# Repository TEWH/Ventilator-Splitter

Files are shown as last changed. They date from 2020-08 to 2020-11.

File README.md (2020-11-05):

Last updated: 9/7/20

NOTE: This is an independent project that is not affiliated with any commercial institution.

# **Table of Contents**
- [Disclaimers](#disclaimers)
- [Background + Why it’s needed](#background-+-why-it’s-needed)
- [Government Policies for Ventilators during COVID-19](#government-policies-for-ventilators-during-covid-19)
- [Materials](#materials)
- [Bill of Materials](#bill-of-materials)
- [Overall Design](#overall-design)
	- [Circuit Design](#circuit-design)
	- [Sensors](#sensors)
- [Electronically-Regulated Valves](#electronically-regulated-valves)
- [Software Design (Valve Control)](#software-design-(valve-control))
- [App Design](#app-design)
- [Low-cost Spirometer](#low-cost-spirometer)
	- [Spirometer Tube](#spirometer-tube)
	- [Circuit](#circuit)
	- [Code](#code)
- [Alarm System](#alarm-system)
- [Limitations & Future Considerations](#limitations-&-future-considerations)

# **Disclaimers**
We are not medical professionals - our design was guided by consultation with biomedical engineering professors from UT Austin and online resources (see References). This should not be used as an equal alternative to a hospital-grade device or reason to delay care from professional health providers. We have created this project for use as an educational resource and platform for commercial organizations to build off of. 

# **Background + Why it’s needed**
Texas Engineering World Health (TEWH) at UT Austin is an organization that is dedicated to making low-cost medical devices and solutions for the developing world. Due to the exhaustion of hospital-grade ventilators and need for emergency solutions due to COVID-19, we decided to design a low-cost ventilator system that allows for multi-patient use (currently: 2 users) in which pressure-controlled ventilation is independently and electronically regulated for each patient. After looking into the [existing solutions](https://docs.google.com/document/d/1PsjM1vYI0WkMa8VHJeYqwy_0DvrdOo4uPSwuuTEJjoY/edit?usp=sharing), our idea was ultimately inspired from [Cornell](https://www.ventilatorsforall.com/about) and [Yale](https://www.medrxiv.org/content/10.1101/2020.04.03.20052217v1)’s ventilator splitter systems. For further details on our brainstorming/design process, see [this link](https://github.com/TEWH/Ventilator-Splitter/tree/master/Brainstorming)

# **Government Policies for Ventilators during COVID-19**
- [FDA Enforcement Policy](https://www.fda.gov/medical-devices/coronavirus-covid-19-and-medical-devices/ventilators-and-ventilator-accessories-covid-19)
- Enforcement Document [PDF](https://www.fda.gov/media/136318/download)

# **Materials**
- Arduino Uno: the microcontroller (two needed - one for each patient)
- Differential Pressure Sensor: for measuring pressure difference in spirometer to calculate volume flow for each patient 
- Servo Motor: for electronic control of pressure gradient (attached to ball valve with 3D-printed connector)
- Absolute Pressure Sensor PCB + 2.54mm Headers: for measuring the pressure values (PIP/PEEP) for each patient 
- LCD Display: To display pressure readings and tidal volume readings as well as any alarm system alerts
- Filter: Needed to prevent any contamination between patients and to filter air before feeding to patient
- PVC/Tubing: Used as the main path for air flow to and from ventilator
- Aquarium Tubing:used to connect the differential pressure sensor to the tubing
- T-Tube connectors: Needed to split the air flow between patients
- PVC Ball Valve: Used to control PIP/PEEP pressure values
- 1-way check valve: Used to prevent contamination of air between patients and to prevent backflow
- Button/Switch: To power on/off the device
- Bellows: Used to simulate the lungs
- Alarm System: To alert doctor if any pressure values or tidal volume is out of range for certain period of time

## **Bill of Materials**
[Updated 8/19/20](https://docs.google.com/spreadsheets/d/1XwOlux3Xf7fFyf_rW_SfKY8QT29Pvu9iuFFEjWML3TM/edit?usp=sharing)

# **Overall Design**
We used a servo motor to regulate affordable valves, and a pressure sensor and a low-cost spirometer to give feedback to the valves of each patient to maintain the appropriate pressure ventilation settings.
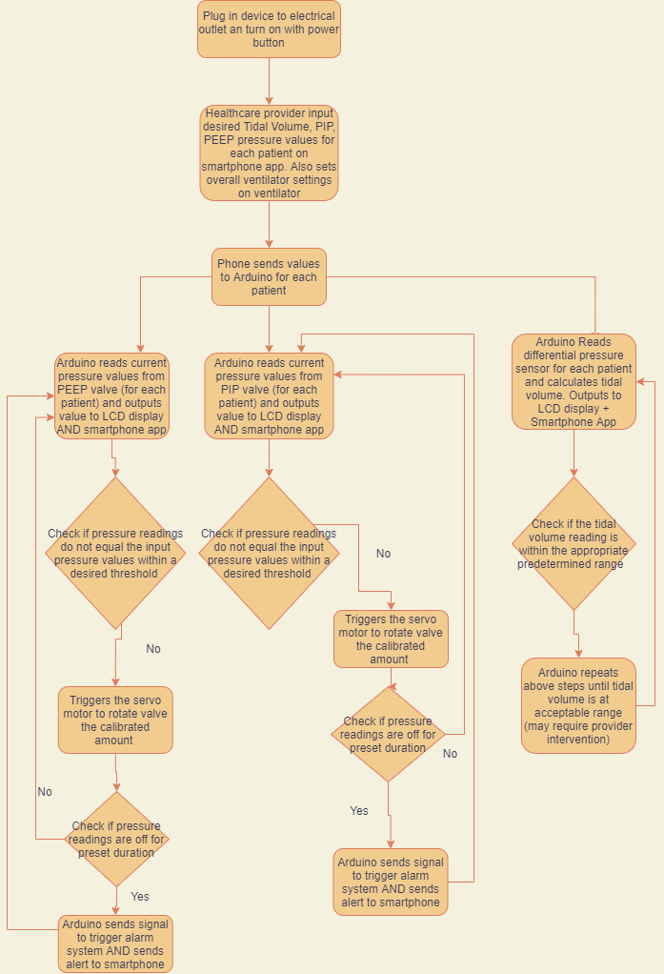
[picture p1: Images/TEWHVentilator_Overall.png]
Overall Flowchart


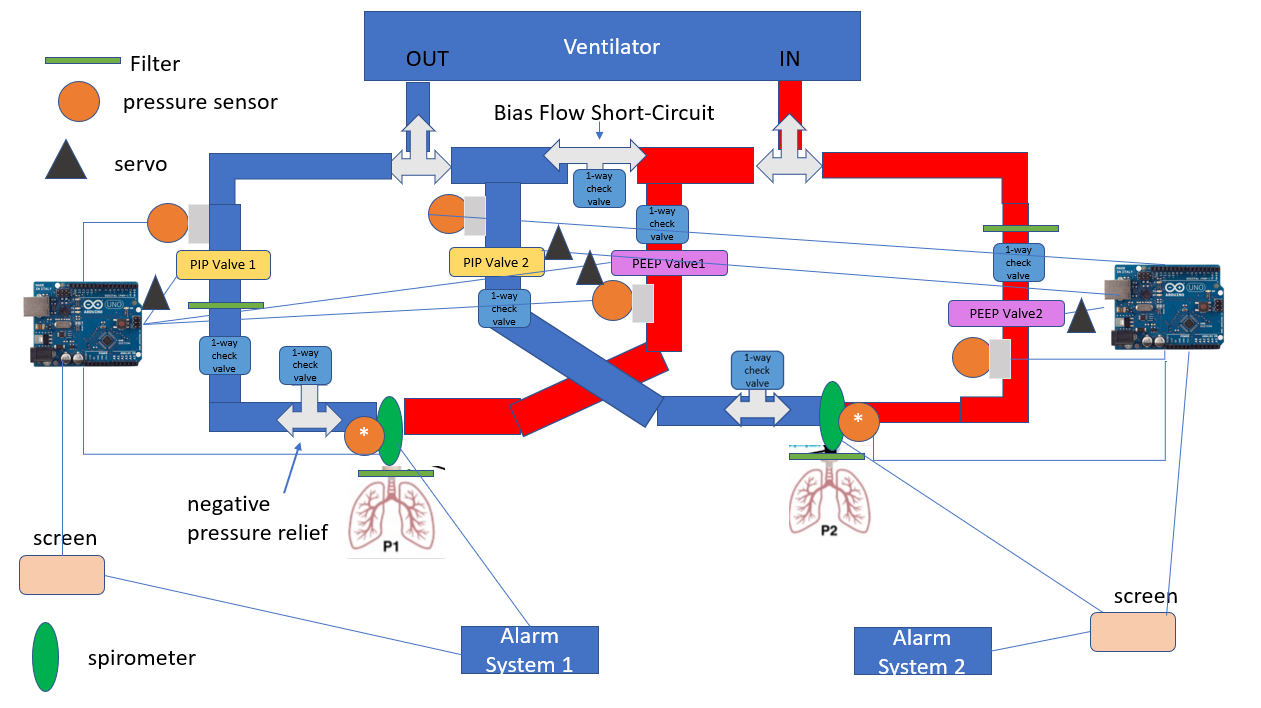
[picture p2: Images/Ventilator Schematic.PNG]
Ventilator Schematic


Put in CAD Designs here 

In this CAD representation, the box represents the ventilator, and one of the pipes coming out is the outflow of air from the ventilator, while the other is the inflow of air. There are t-tubes to separate the flow of air out of the ventilator and into the ventilator from each patient. In addition, there are ball valves acting as the PIP/PEEP valves for each patient, all connected to their own servo motor. There are also absolute pressure sensors (represented by the rectangles on the pipes). These pressure readings are repeatedly sampled and checked to verify that they are at the appropriate threshold. The Arduinos (not pictured in this CAD file) would be connected to the servos as well as the pressure sensors, so that if the pressure is not at the desired level, the servo would turn the ball valve the appropriate amount to adjust. At the end of the pipes, there is the spirometer, represented by the vertical cylinder. This has a differential pressure sensor which would be connected to the Arduino for the respective patient. Both the spirometer and the PIP/PEEP valves would be connected to the alarm system (consisting of a buzzer and an LCD screen) as well as the bluetooth module which connects to the app. There are also one way check valves that are incorporated to prevent contamination between patients, and it is also where filters would be added in the actual design.

## **Circuit Design**
The design utilizes one Arduino Uno Rev.3, two servo motors, two absolute pressure sensors, one differential pressure sensor, a LCD, a piezo-buzzer, a pushbutton switch, and one HC-05 bluetooth module for each patient. Both the PIP valve and the PEEP valve each consist of one servo motor and one absolute pressure sensor, while the spirometer makes use of the differential pressure sensor and the LCD. The piezo-buzzer and the pushbutton switch make up the alarm system, which also makes use of the LCD as well. The HC-05 bluetooth module enables the ventilator splitter to send and receive data from an app. 

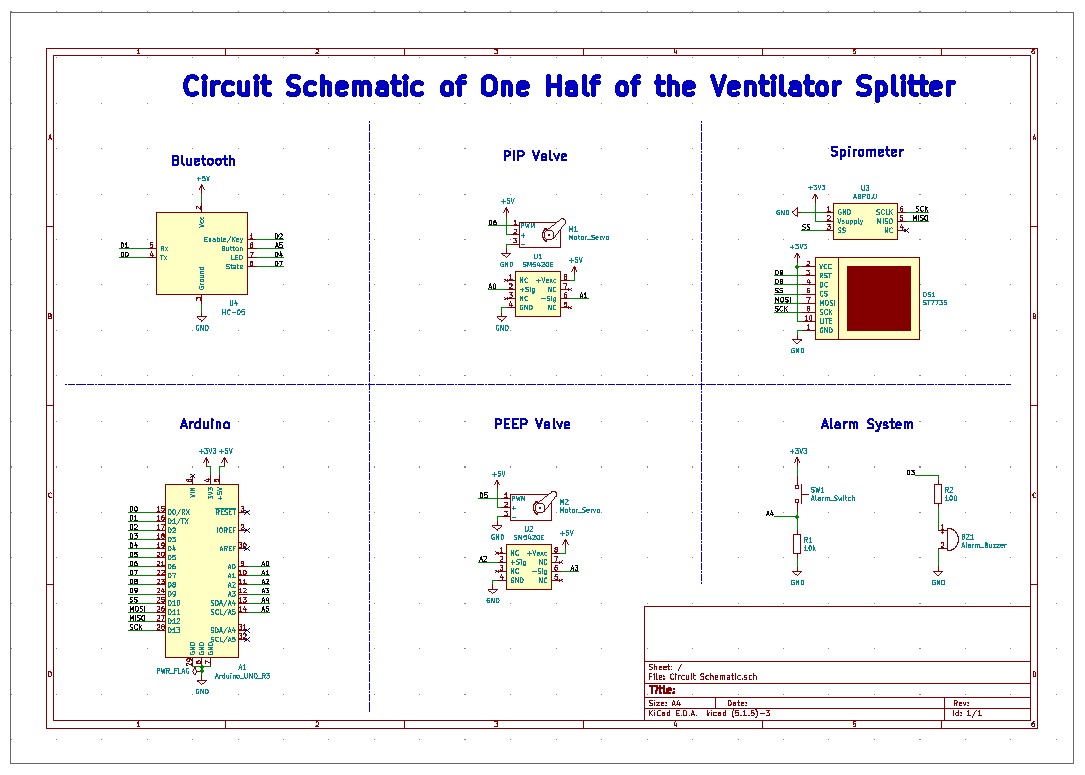
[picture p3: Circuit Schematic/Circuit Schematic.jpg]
Circuit Schematic Image

*Figure: Circuit schematic corresponding to one patient*

### *Arduino Connections*
Pins 10, 11, 12, and 13 of the Arduino Uno are dedicated for Serial Peripheral Interface communication protocol (SPI) use, corresponding to the slave select (SS), master out slave in (MOSI), master in slave out (MISO), and the clock (SCK) connections respectively. The absolute pressure sensors are connected to the analog pins of the Arduino, while the remaining connections of the servo motors, differential pressure sensor, and the LCD display are to the digital pins. 

### *Servo Motors*
The servo motors used for the PIP and PEEP valves are controlled using pulse-width modulation (PWM) connections to any GPIO pins of the Arduino and are powered off the +5V line of the Arduino. The other two connections to the servo motors are to power (+5V) and ground. 

### *Absolute Pressure Sensor* 
The absolute pressure sensors in the PIP and PEEP valves are connected to two analog pins of the Arduino each, and like the servo motors, they are powered using the +5V line of the Arduino. Though there are eight pins to the component, the only other connections required are to power (+5V) and ground. 

### *Differential Pressure Sensor*
The differential pressure sensor used in the spirometer is controlled by the Arduino using SPI and is powered using the +3.3V line of the Arduino. Beyond the SPI connections, the sensor is also connected to power (+3.3V) and ground. 

### *LCD*
The LCD is controlled by the Arduino using SPI and is also powered using the +3.3V line of the Arduino, much like the differential pressure sensor. The backlight pin is connected to the +3.3V line, while the reset and data-command pins are connected to the digital pins of the Arduino. Its remaining connections are to power (+3.3V) and ground. 

### *Piezo-Buzzer*
The piezo-buzzer used in the alarm system is connected to a PWM pin on the Arduino. A resistor is connected to the piezo-buzzer as well in order to protect the microcontroller from any damage due to the buzzer. The buzzer is also connected to ground. 

### *Pushbutton Switch*
The pushbutton switch used in the alarm system is connected to the Arduino in a positive logic configuration and thus is connected to a pull down resistor. The switch is also connected to power (+3.3V). 

### *HC-05 Bluetooth Module*
The bluetooth module used to communicate with the app is connected to the serial pins of the Arduino (D0 and D1), as it uses the Universal Asynchronous Receiver/Transmitter (UART) communication protocol. Its Enable/Key, Button, LED, and State pins are all connected to digital pins of the Arduino. The bluetooth module is powered by the +5V line and is connected to ground as well. 

## **Sensors**

### *Absolute Pressure Sensor* 
The absolute pressure sensors are used in the PIP and PEEP valves to measure the pressure during inhalation and exhalation respectively. Due to its low cost and small size, the [SM5420E series board mount sensors](https://www.mouser.com/datasheet/2/589/SM5420E_40ds5468.02_1-1100662.pdf) from Silicon Microstructures, Inc. (Manufacturing Number: 5420E-030-A-P-S) were chosen. The typical ranges of PIP and PEEP is well within the operating pressure of the sensor (30 PSI). However, since the pressure sensor is intended to be a surface mount component, a PCB was created to make it functional within this design. 

The PCB can be found within this Github repository. Its design consists of the footprint for the sensor and 2.54mm headers to connect the sensor to the Arduino Uno. 

Circuit Schematic Image
*Figure: Circuit Schematic of the PCB*

### *Differential Pressure Sensor* 
One differential pressure sensor is used in each spirometer in order to measure the difference between the pressure during inhalation and that during exhalation. This measurement can be used to calculate the respiratory flow rate and the tidal volume by converting the pressure difference into a voltage, which is then processed and manipulated in the code. 

The differential pressure sensor chosen for this application is the [SMT JJ Basic Board Mount Pressure Sensor](https://www.mouser.com/datasheet/2/187/honeywell-sensing-basic-board-mount-pressure-abp-s-1662208.pdf) from the ABP Series. The operating pressure of 15 PSI includes the expected pressures that will be measured. Additionally, its small size makes it a decent differential pressure sensor for the spirometer.  

## **Electronically-Regulated Valves**

One of the most notable mechanical components of this design include the four ball valves which effectively serve as PIP (Peak Inspiratory Pressure)/PEEP (Peep Expiratory Pressure) valves. The purpose of the PIP valve for each patient is to maintain the highest level of pressure to the lungs during inhalation and the purpose of the PEEP valve for each patient is to maintain pressure on the lower airways during exhalation so the alveoli do not collapse. 

Ball valves were chosen for this design because they can achieve fast opening and closing (0.05 - 0.1 s), have a large pressure range, and are affordable compared to other options. 0.5 inch ball valves were used, as they had a maximum working pressure of 150 PSI which is well within the ventilator pressure range. For this project, the pressure provided by the ventilator was assumed to be about 40 cmH2O based on the Yale design.

To control the ball valves electronically, servo motors were used. The servo motors have a control angle of 270 degrees, and a large torque up to 21.5 kg/cm--enough to move the ball valves open and closed. The motor controls how much the valve knob turns, depending on the extent of pressure change needed. This is unique in that the motor can actively control pressure as a gradient rather than just on/off.

Other materials used as a proof-of-concept design include PVC pipes and T-tube splitters to act as the tubing. 

## **Software Design (Valve Control)**  
Below you can see a flowchart for the software design of the valve control. There is a high level of control given to the doctor to make sure that settings can be individualized.

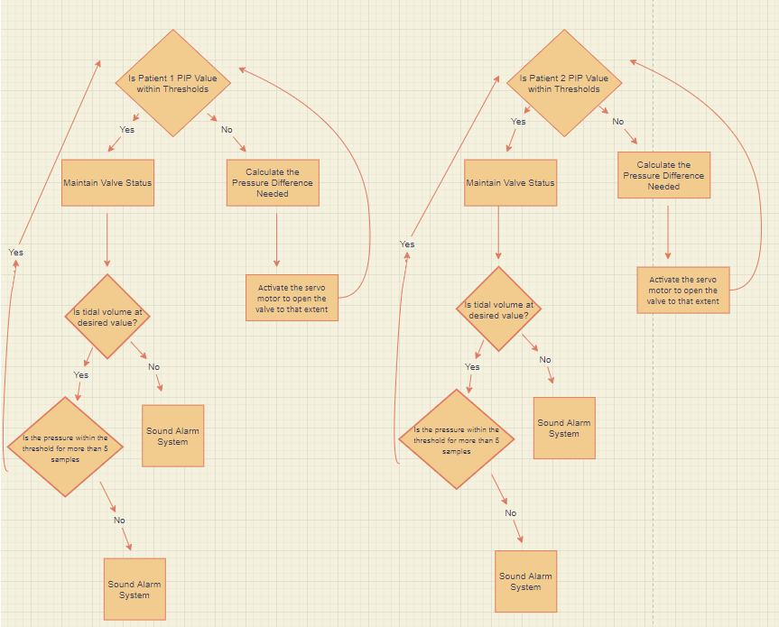
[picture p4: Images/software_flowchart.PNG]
Software Valve Control


## **App Design**
Below is the design of the App screens. 
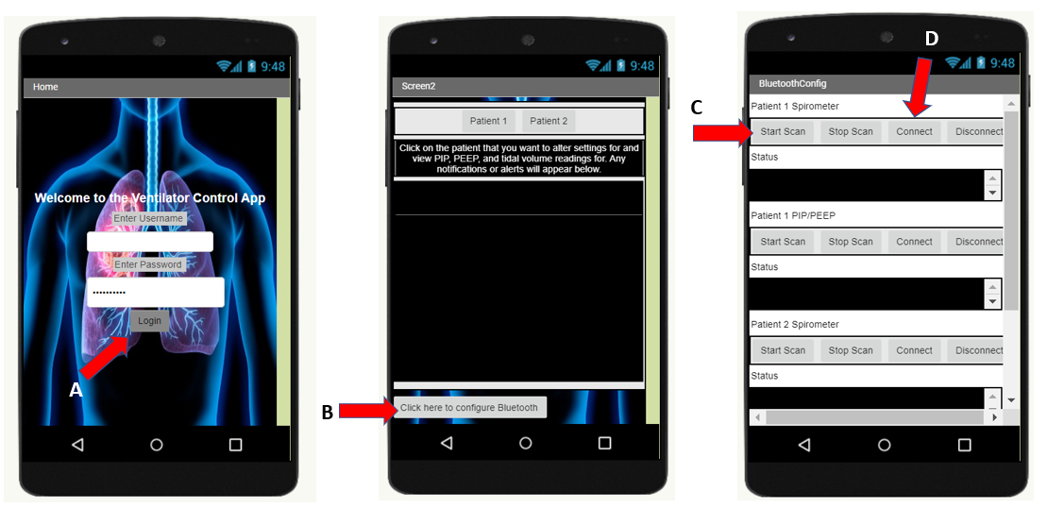
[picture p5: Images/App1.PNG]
App1
 
The Home screen of the app will have security and a login (probably integrated with whichever hospital system is using this). Then, it will open up screen 2, which is an overview of any important notifications, and which has a button to configure bluetooth. If bluetooth is already configured, one may click on Patient 1 or Patient 2 to open up their settings. On the third screen, when the “Start Scan” button is pressed, the app displays “Scanning” under status and lists the possible bluetooth connections. Then, when “connect” is pressed and a particular bluetooth option is selected, the settings that were configured will be sent to the Arduino, and the readings from the sensors will be sent back to the phones. There are different bluetooth connection settings for each patient’s PIP/PEEP readings as well as their tidal volume readings coming from the spirometer. 
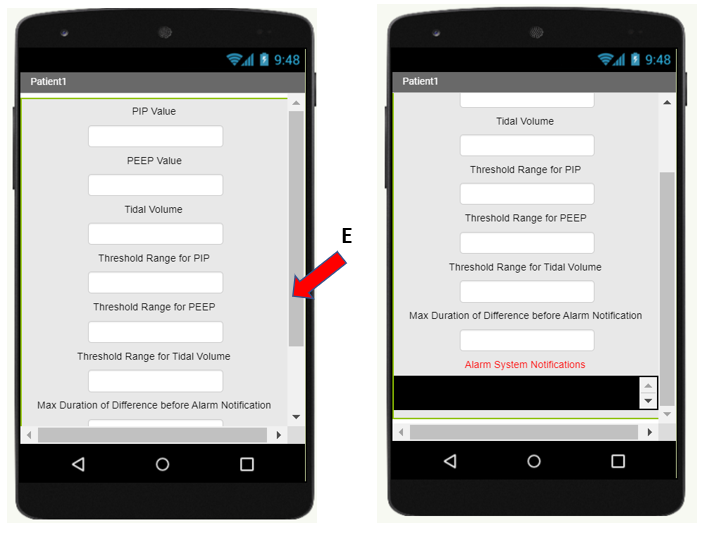
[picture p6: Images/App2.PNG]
App2
 

These screens show the settings (for Patient 1 in this case). The healthcare provider can enter these in and they will be synced to the Arduino. There will also be patient specific notifications and readings on this page.

Below is the basic code for how the Bluetooth scanning and connection would occur.
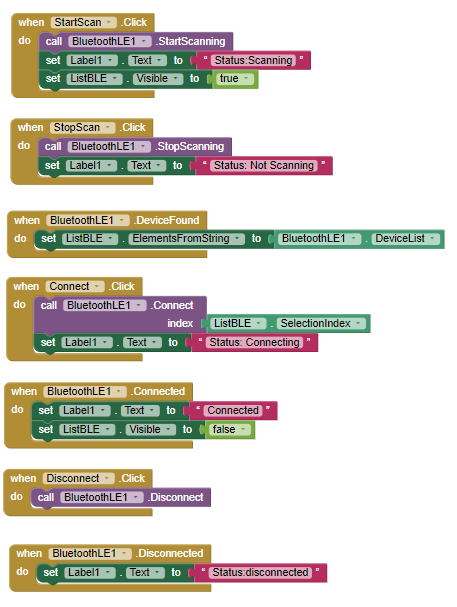
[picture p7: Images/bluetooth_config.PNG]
Bluetooth Config
 

# **Low-cost Spirometer**
Designing a low-cost spirometer was inspired by this [Instructable](https://www.instructables.com/id/Low-Cost-Spirometer/). 
The spirometer is typically used for assessing respiration and diagnosing pulmonary disease. In our case, we are including it in our ventilator system to calculate the tidal volume of each patient.
  
## *Spirometer Tube*
Plastic pipes (e.g. PVC) are recommended for constructing the spirometer “tube”, but due to lack of available resources, cardboard tubes were used instead. 
Two pipes with a significant diameter difference are needed. The smaller diameter tube will be placed inside the larger diameter tube to create the needed pressure drop across the section where the diameters change. 
- Measure the diameters of the two pipes - these values will later be used to calculate the pressure drop
- Cut two pieces of aquarium tubing (~1 ft) long
- Drill or cut a small hole that is roughly the diameter of the aquarium tubing on each side of the diameter change. 
- Insert each aquarium tubing piece into a cut hole. The aquarium tubing will be used to connect the differential pressure sensor to both sides of the diameter change region. -- - With foam or cotton (or another appropriate material), plug the empty space in between the two pipes
- Once the aquarium tubing is properly inserted and positioned, tighten the seals using hot glue. 

## *Circuit*
Aside from the LCD screen and Arduino microcontroller, the pressure sensor is the only other major circuit component. We used a differential Honeywell Board Mount Pressure Sensor (ABPDRRV015PDSA3 - datasheet found [here](https://www.mouser.com/datasheet/2/187/honeywell-sensing-basic-board-mount-pressure-abp-s-1662208.pdf)).
Differential pressure sensors measure pressure differences and convert them into voltages. These voltages are sent to an Arduino microcontroller, which calculates the pressure drop and tidal volume and sends it for display on the LCD screen. The sensor itself has two ports where pressures can be applied. Below is the transfer function that can be arranged to calculate the pressure difference based on the sensor’s output voltage. 

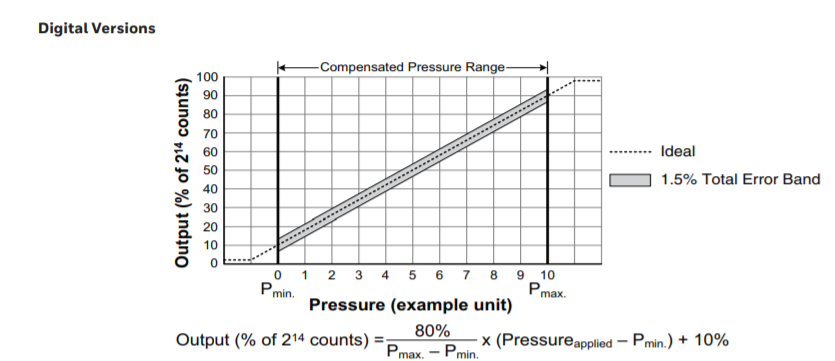
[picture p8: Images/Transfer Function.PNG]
Transfer Function for Digital Sensor


*Transfer Function for Digital Sensor: Takes pressure difference and converts into an output voltage*

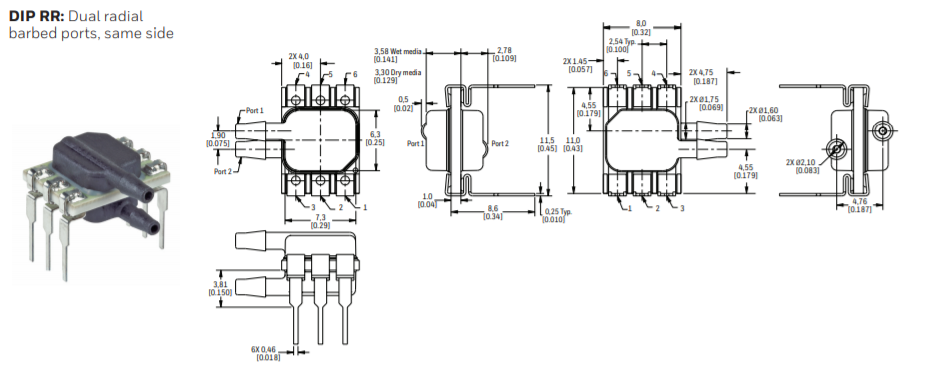
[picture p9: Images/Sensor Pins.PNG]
Pin Layout for Pressure Sensor


*Pin Layout for Pressure Sensor (First diagram is the top view)*

Pin configuration (Pressure Sensor → Arduino Uno) - See below images for more detail: 
Pin 1 → GND
Pin 2 → Voltage supply (3.3 V)
Pin 3 → SS (Slave Select Pin) - Pin 10 
Pin 5 → MISO (Master In Slave Out) -  Pin 12
Pin 6 → SCLK (Serial Clock) - Pin 13

Pinout for Pressure Sensor

*Pinouts for Pressure Sensor (our selected sensor uses SPI)*

## *Code*
An important point to note is that the output type of the pressure sensor (e.g. analog vs. SPI) will affect the syntax of the code. As our sensor uses Serial Peripheral Interface (SPI) communication, our code has been written accordingly. 

A brief overview of SPI (more details [here](https://www.arduino.cc/en/reference/SPI)): it is used by microcontrollers for quickly communicating with peripheral devices over short distances. With SPI, a master device (e.g. an Arduino) controls peripheral devices (e.g. pressure sensor) typically using these lines: 
- SCK (Serial Clock): sends clock pulses, synchronize data transmission
- MISO (Master In, Slave Out): peripheral device sends data to master
- MOSI (Master Out, Slave In): master sends data to peripheral devices 
There is also a line used to control a peripheral device
- SS (Slave Select) pin: activates or disables a specific device

For any new SPI circuit device, refer to its datasheet to make note of the following:
- Maximum SPI speed (e.g. 15 MHz)
- Is the data shifted in either Most Significant Bit or Least Significant Bit  
- Clock polarity (clock) and clock phase (is data sampled on either the rising or falling edge of clock pulses)

Once these have been identified, the SPI settings can be configured using this command: SPI.beginTransaction(SPISettings(800000, MSBFIRST, SPI_MODE0));

Note: the following code outputs its values to the Serial Monitor, but can be modified to display its output to an LCD screen: 

```cpp
#include <SPI.h>
```
This imports the SPI library needed to communicate with the pressure sensors

```cpp
 float pressure_psi; // Pressure value calculated from voltage, in psi
 float pressure_pa; // Pressure converted to Pa
 float massFlow; // Mass flow rate calculated from pressure
 float volFlow; // Calculated from mass flow rate
 float volume; // Integral of flow rate over time

 //Constants
 float rho = 1.225; // Density of air in kg/m3
 float area_1 = 0.004536; // C.S.A. of larger tube in m2 
 float area_2 = 0.001257; // C.S.A. of smaller tubein m2
 float dt;

void setup() {
  
  Serial.begin(9600);
  pinMode(10,OUTPUT);
  
  // start the SPI library:
  SPI.begin();
  
  /*Honeywell digital output pressure sensors are configured for
  operation such that data on the MISO line will transition during
  the falling edge of clock pulses. This means that the data on
  MISO should be sampled by the master device during the
  rising edge of the clock pulse.
  */
    
  SPI.beginTransaction(SPISettings(800000, MSBFIRST, SPI_MODE0)); 
}
``` 
Now that the appropriate constants and SPI settings have been configured, the following code details how to convert a voltage signal into an air volume: 
```cpp
void loop() {
  
  delay(1000);
  //Activate Slave Select line
  digitalWrite(SS, LOW);
  //Read Sensor
  int inByte_1 = SPI.transfer(0x00);  // Read first Byte of Pressure
  int inByte_2 = SPI.transfer(0x00);  // Read second Byte of Pressure
  //Disconnect Slave
  digitalWrite(SS, HIGH);
  SPI.endTransaction();
  
  //Print Pressure Readings in Counts
  Serial.print("Byte_1 = "); Serial.print(inByte_1, DEC); Serial.print(" ");
  Serial.print("Byte_2 = "); Serial.print(inByte_2, DEC); Serial.println(" ");

  //Combine both pressure reading bytes 
  int pressure = inByte_1 << 8 | inByte_2; // Note: the pressure output for this specific sensor is 12 bits
  Serial.println(pressure);

  //Convert pressure in bytes to float
  float convert = float(pressure);  

  //Calculate pressure in psi
  pressure_psi =  (((30)*(convert - 1638) / 13107) - 15); // +/- 15 psi is the pressure range
  Serial.print("Pressure = "); Serial.println(pressure_psi);
  
  // Convert pressure to Pa
  float pressure_pa = pressure_psi*6894.75729; 
  
  // Mass flow of air (kg/s)
  massFlow = 1000*sqrt((abs(pressure_pa)*2*rho)/((1/(pow(area_2,2)))-(1/(pow(area_1,2))))); 
  
  // Volumetric flow of air
  volFlow = massFlow/rho; 
  
  // Total volume (essentially integrated over time)
  volume = volFlow*dt + volume; 
  dt = 0.001;
  delay(1);
  
  Serial.print("Volume = "); Serial.println(volume);
```
# **Alarm System** 
The Alarm System makes use of a piezo-buzzer, a pushbutton switch, and the LCD. While the Ventilator Splitter is in use, the Alarm System regularly checks the differential and absolute pressure sensor data in order to check whether the pressure is outside of the acceptable input range. 

If the pressure is within the range, the Alarm System continues to loop. However, if the pressure falls outside the acceptable range, the Alarm System will trigger the piezo-buzzer to start beeping, and it will continue to do so while the pressure is outside the acceptable range or until the pushbutton switch is pressed to override the Alarm System.

Additionally, if the Alarm System is triggered, it will display what pressure measurement triggered the Alarm System on the LCD, and it will notify the user and send this message to the app as well.

For the circuit schematic of the Alarm System, see [Circuit Design](#circuit-design), and for the details on the software, see [Overall Design](#overall-design). 

# **Limitations & Future Considerations**
One of the greatest limitations for this project was the barriers to testing. All of the components were prototyped remotely, and with public health regulations in mind, we are currently unable to run testing. Our system needs to be compared against medical-grade equipment to validate the accuracy of tidal volume measurements and ventilator pressure profile, and so this project's documentation is meant to serve as a proof-of-concept. 
In addition to robust testing, the processing speed of our system could be greatly improved by creating a real-time operating system that allows multiple threads to run in parallel and customized prioritization of tasks.

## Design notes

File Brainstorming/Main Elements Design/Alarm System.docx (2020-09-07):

Design

- For both pressure and tidal volumes.
- If pressure and/or tidal volumes are out of bounds and the internal negative feedback loop cannot restore these parameters, operator of ventilator alerted.
  - Manual override for pressure valves in the case of an alarm
- Could use a piezoelectric buzzer? Need a loud one so the alarm is easily heard. A flashing light would also grab attention.
- https://create.arduino.cc/projecthub/SURYATEJA/use-a-buzzer-module-piezo-speaker-using-arduino-uno-89df45 - Code and simple circuit for buzzer
  - Is there a way to have two different buzzer noises indicative of either high or low pressure? In addition we could have a screen that says high/low pressure depending on the situation.
- Useful link for a video on ventilator settings for nurses (https://www.youtube.com/watch?v=I8KH68fR0gI)

From that I gathered that there are two major things the ventilator tracks:

Low pressure Alarm/ Low minute ventilation :

- Disconnection
- Cuff Leak - cuff pressure manometer on ET tube (no greater than 20 cm h2o usually 8-20)
- Tube Displacement

High pressure Alarm :

- Excess secretions → need suction
- Biting
- Kinks
- Coughing
- Pneumothorax
- Bronchospasm

https://www.youtube.com/watch?v=WtwDp4f0pqU 9:42 - high tidal volume alarm

- Based on the Yale design’s proposed alarm settings:
  - Individual Vte low alarm: Vte - 50 mL, high alarm = vte + 50 ml
  - High pressure alarm
  - Low pressure alarm

Typical Initial Ventilator Settings (https://www.ncbi.nlm.nih.gov/books/NBK448186/) (look at the clinical significance section)

This seems to be good (https://emcrit.org/wp-content/uploads/vent-handout.pdf)for specific values (need to go back and read it more)

- It is started with an FiO2 of 100% and titrated down guided by pulse oximetry or ABG, depending on the case.
- Low tidal volume ventilation has been shown to be lung protective not only in ARDS but in other types of diseases. Starting the patient on a low tidal volume (6 to 8 mL/Kg of ideal body weight) will reduce the incidence of ventilator-induced lung injury (VILI).
  - Always use a lung protective strategy as there are not many advantages for higher tidal volumes and they will increase shear stress in the alveoli and may induce lung injury.
- Initial RR should be comfortable for the patient 10-12 bpm should suffice.
  - A very important caveat on this is for patients with severe metabolic acidosis. For these patients, the minute ventilation should at least be matched to their pre-intubation ventilation as failure to do so will worsen acidosis and can precipitate complications such as cardiac arrest.
- Flow should be initiated at or above 60 L/min to prevent auto-PEEP.
- Start with a low PEEP of 5 cm H2O and titrate up as tolerated by the patient to the goal for oxygenation. Pay close attention to blood pressure and patient comfort while doing this.
- An arterial blood gas should be obtained 30 minutes after intubation and changes to the ventilator settings should be made in accordance with ABG findings.
- Peak and plateau pressures should be checked on the vent to assure there are no problems with airway resistance or alveolar pressure in order to prevent ventilator-induced lung injury.
- Attention should be given to the volume curves in the ventilator display as a reading showing that the curve is not coming back to zero at the time of exhalation is indicative of incomplete exhalation and development of auto-PEEP and corrections to the vent should be made immediately.

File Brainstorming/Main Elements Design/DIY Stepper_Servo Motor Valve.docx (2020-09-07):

Ways to Regulate Pressure:

- Regulate pressure using negative feedback from only the spirometer (tidal volume). Pressure adjusted to get correct tidal volume.
- Regulate pressure using input from a combination of pressure sensors and spirometer, so both pressures and tidal volume are in the acceptable range.

Design Ideas/Implementation:

- https://physics.stackexchange.com/questions/95620/how-does-pressure-of-a-fluid-change-with-area-according-to-the-continuity-equat
  - Decrease cross-sectional area → pressure decreases
- Pressure Range Needed:
  - Normal patients: Normal lung compliance is around 100 ml/cmH20. This means that in a normal lung the administration of 500 ml of air via positive pressure ventilation will increase the alveolar pressure by 5 cm H2O. Conversely, the administration of a positive pressure of 5 cm H2O will generate an increase in lung volume of 500 mL
- DIY Stepper Motor
- DIY Servo Motor

https://www.instructables.com/id/Arduino-Servo-Motors/

https://www.tutorialspoint.com/arduino/arduino_servo_motor.htm

- Solenoid Valve + Microcontroller - https://hackaday.io/project/148274-electronic-pressure-regulator

https://www.bc-robotics.com/tutorials/controlling-a-solenoid-valve-with-arduino/

- Using a servo motor + force sensor (?) https://cdn.sparkfun.com/datasheets/Sensors/ForceFlex/2010-10-26-DataSheet-FSR400-Layout2.pdf
- FLUID FLOW BASICS OF THROTTLING VALVES (https://www.controlglobal.com/assets/Media/MediaManager/RefBook_Cashco_Fluid.pdf)
- fundamentals-valves-types (https://instrumentationtools.com/fundamentals-valves-types/)

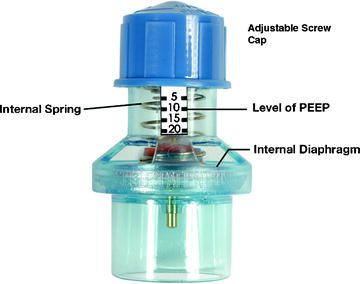
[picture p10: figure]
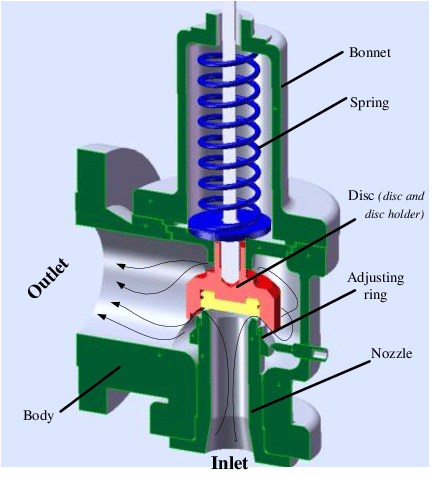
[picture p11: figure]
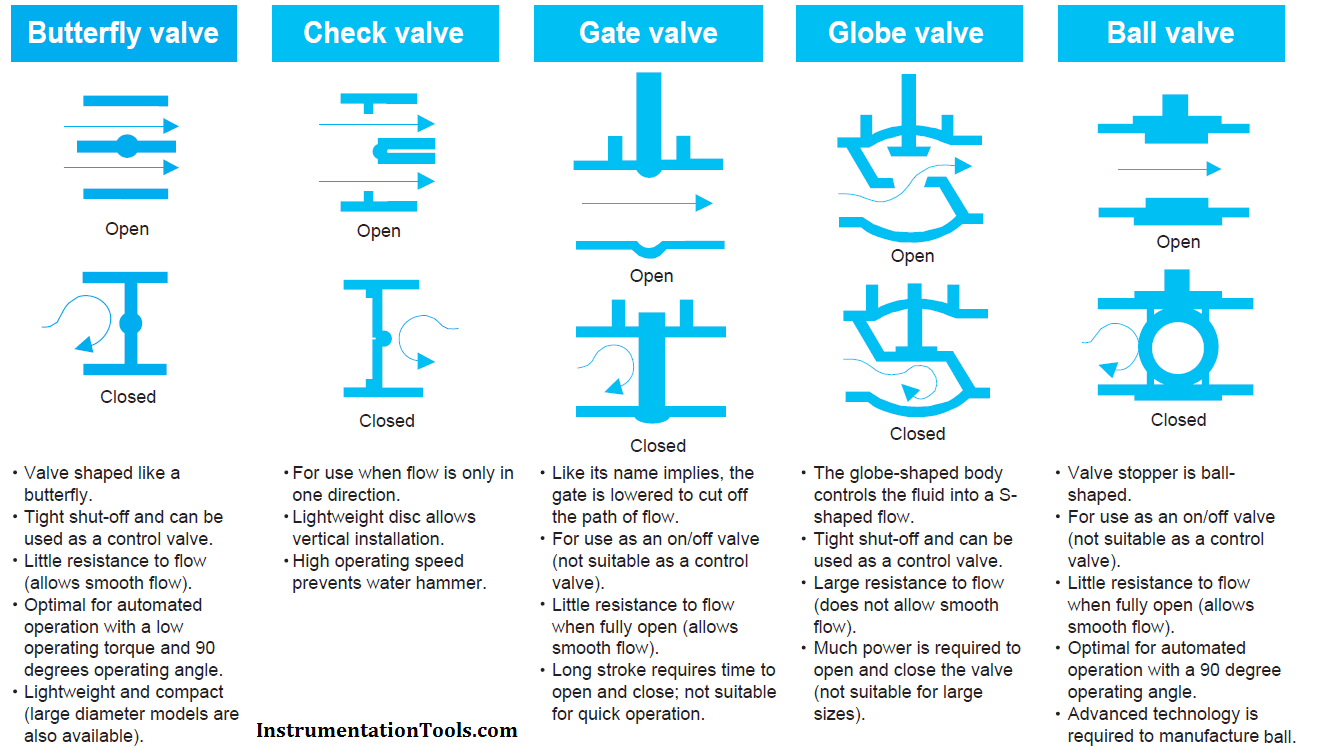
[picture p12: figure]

Testing:

Materials:

- From the video (https://www.youtube.com/watch?v=2vAoOYF3m8U) from last time:
  - 3D Parts: https://www.thingiverse.com/thing:3170748
  - 3D Parts: https://www.myminifactory.com/object/3d-print-77542
  - Servos: https://www.amazon.com/FEETECH-FS90R-Pack-Continuous-himalayanelixir/dp/B07824TSXB/ref=psdc_2234131011_t1_B074BFQC3Q
  - Epoxy: https://www.amazon.com/gp/product/B005UYVIXO/ref=as_li_tl?ie=UTF8&tag=potentprintab-20&camp=1789&creative=9325&linkCode=as2&creativeASIN=B005UYVIXO&linkId=4604264d0434a096933684226449351d
  - Arduino Uno
  - Adafruit Motor/Stepper/Servo Shield (https://www.amazon.com/gp/product/B00PUTH3B0/ref=as_li_tl?ie=UTF8&tag=potentprintab-20&camp=1789&creative=9325&linkCode=as2&creativeASIN=B00PUTH3B0&linkId=68c63b4bb33a5eaaa4cf3d79c7247bc4)

3D Printing Sources:

- List of Sources: https://www.makepartsfast.com/outsourcing-options-for-3d-printing/
- Pros and Cons of Different Sources: https://www.howtogeek.com/303866/how-to-3d-print-anything-even-if-you-dont-own-a-3d-printer/
  - Shapeways: This is good if you need a professional’s opinion and has people that can help, but it may be more of a place to shop for already designed 3D parts. It is possible to print your own designs though.
  - 3D Hubs: You can shop around to find the best printer source, but there’s not much you can do for quality control (there’s a money-back guarantee though that addresses this). The best pro is its speedy delivery time, which would be good for us.
  - Sculpteo: You can order your models in bulk, which might be helpful in the future.
- From a previous meeting, there was also a Google Sheets with many people volunteering their 3D printers to be used. I couldn’t find the link, but this might be nice, given that we are all working at different places and could then all of us could work on it.

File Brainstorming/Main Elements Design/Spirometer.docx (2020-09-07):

Design

https://www.instructables.com/id/Low-Cost-Spirometer/

Main Materials:

- PVC pipe
- Plastic tubing
- Pressure Sensor: most implementations like the instructables link above use this ASDX Silicon Differential Pressure Sensor https://eu.mouser.com/Honeywell/Sensors/Pressure-Sensors/Board-Mount-Pressure-Sensors/ASDX-Series/_/N-6g7qs?P=1yzrzfxZ1z0sf9t

But very expensive ($50+). Differential pressure sensors convert a pressure difference to a voltage, so they are convenient.

Alternative is to use two of these: https://learn.adafruit.com/adafruit-mprls-ported-pressure-sensor-breakout

They are ported, which is what we need. Would need to read the two pressure values individually instead of having one sensor directly outputting the delta pressure.

Flow Chart/Diagram

In folder

Pseudocode

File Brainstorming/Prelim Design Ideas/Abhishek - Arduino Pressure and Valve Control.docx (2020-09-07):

Arduino Pressure and Spirometer With/Without Valve Control

Addressed Concerns from Cornell Redesign Research Doc: Improve upon the crude nature of the Cornell Design (manual pressure gauges/spirometers) - is there a way to make this more seamlessly integrated? Some sort of software to plug into a ventilator that seamlessly provides specific pressure/volume to different tubes? We may even be able to add a spirometer to assist with tidal volume measurements, and some sort of alert system if any of these things are changed so doctors don’t have to constantly be monitoring this

The CO2 monitor can be used to also alert doctors for hypercapnia or hypocapnia (pH of blood/gas)

Without Valve Control: The standard Cornell design uses analog pressure gauges and spirometers. This idea aims to digitize all the sensors, display the data on a screen, and alert the medical professional if any of the parameters go out of bounds. This will massively cut down on the time needed for the medical professional to operate the ventilator as all the information is displayed centrally on a screen, and the medical professional would not have to constantly check on the pressure gauges with the alert system. This system would also enable adding CO2/O2 sensors as well, if needed. The pressure valve controller would be a manual one, where the operator would turn it to adjust the pressure.

Pressure Sensor (I am not completely sure if this will work for the pressures needed in a ventilator. Measures up to 8.75 kPa above atm): https://www.adafruit.com/product/1603

https://learn.sparkfun.com/tutorials/bmp180-barometric-pressure-sensor-hookup-/all

Spirometer: https://www.instructables.com/id/Spirometer/

https://www.instructables.com/id/Low-Cost-Spirometer/

With Valve Control: This would involve a negative feedback loop between the pressure sensors and the valve controller. This is more complex as we would need to build an electronic pressure valve controller. However, this would eliminate the need for anyone to keep manually adjusting the pressure valve, as this would be done by the Arduino electronically. The pressure valve would most likely be a solenoid valve.

Valve Control Ideas: https://www.instructables.com/id/Pressure-Control-Using-Arduino/

https://www.bc-robotics.com/tutorials/controlling-a-solenoid-valve-with-arduino/

https://www.instructables.com/id/Controling-a-solenoid-valve-with-an-Arduino/

Rough sketch on next page->

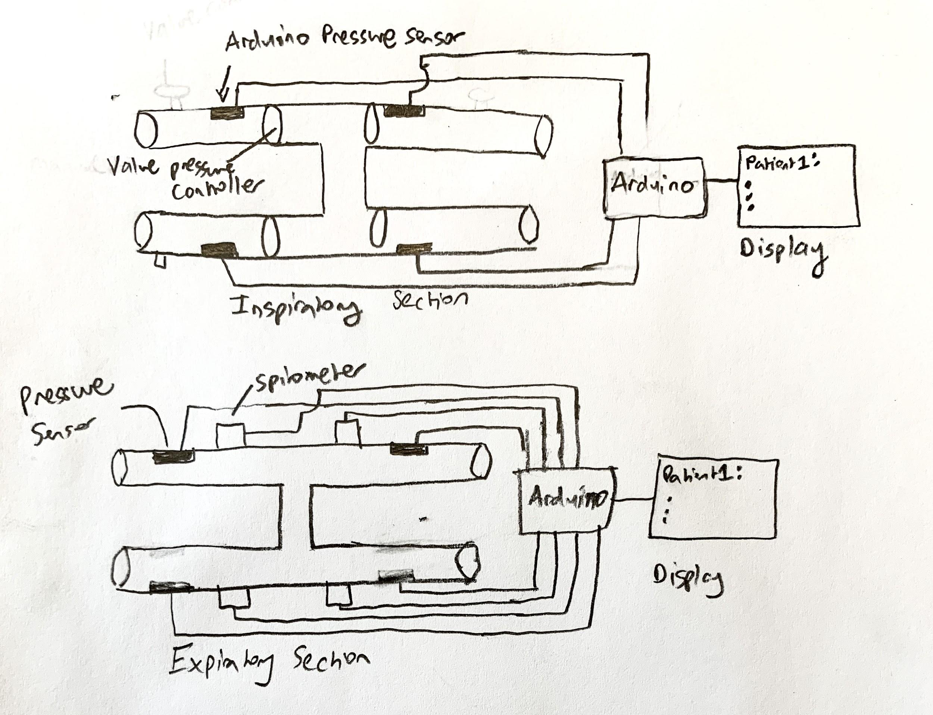
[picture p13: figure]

*Assumes the “H” design for now.

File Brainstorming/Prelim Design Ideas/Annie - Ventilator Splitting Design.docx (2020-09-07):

Materials:

- Arduino
- Wires or bluetooth??
- LED Display
- HEPA filter
- 1-way valves
- Balloon (to mimic lung)
- Compressed air
- Buzzer?
- Pressure gauge
- Spirometer ? or Co2 sensor
- O2 bleed ins - if we want to account for hypoxia

Design:

Pretty much just an add-on and more convenient set up for doctors so they don’t have to assemble the splitting of the ventilator and look through guidelines etc. Can have a display on Arduino that shows the normal outputs the actual machine would but for each individual patient. I’m still trying to figure out what sensors we could use to measure efficiency of ventilation (i.e. whether we want to incorporate pressure gauge/spirometer?) bc if we are able to predict purely based on CO2 expired that might be a better option.

driving pressure ~ [ (peak pressure) – peep ]

These were some ideas from the link we might be able to incorporate:

- increase FiO2 levels on individual lines with a variable valve based on inputs from an oximeter or CO2 sensor?
- Individual differences in hypoxia could be addressed by separate O2 bleed ins. This way, ventilation and oxygenation could be easily adjusted to individual patients without the possibility of cross contamination.
- line consisting of a manual pinch valve and a differential pressure sensor (before and after valve) which enables specific pressure support adjustment and also an estimate of tidal volume (thru calibration of pinch valve characteristic vs delta P). More complex than just an arrangement of splitter connectors – but much more functional I think.

https://www.sciencedirect.com/science/article/pii/S0007091217344471

https://www.ncbi.nlm.nih.gov/pubmed/29351442

https://www3.gehealthcare.com/~/media/downloads/us/product/product-categories/anesthesia-delivery/gehc_technical-report_pressure-control-ventilation-volume-guaranteed.pdf

How to maintain unchanged tidal volumes from Yale experiment- As is clear from Figure 12, decreased compliance in Patient #1 could be largely offset, in terms of resulting tidal volume, by titrating the pressure on for Patient #1 on the inspiratory limb. In this study, the tidal volume for Patient #1 was maintained at approximately 330 mL, by means of decreasing the pressure-gated valve set point on the inspiratory limb from

17 to 5 cmH2O as the lung compliance fell. But despite the fact that the setting on the pressure-gated inspiratory valve for Patient #1 was being decreased, the inspiratory pressure and tidal volumes for Patient #2 remained unchanged. This experiment illustrates the potential feasibility of maintaining tidal volumes in one patient with changing lung mechanics, while not affecting the ventilation of the other patient treated with the PReVentS circuit.

https://www.medrxiv.org/content/10.1101/2020.04.03.20052217v1.full.pdf - These people p much did what we’re trying to do :-)

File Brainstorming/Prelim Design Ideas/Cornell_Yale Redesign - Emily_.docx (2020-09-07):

Materials

- Electronic Parts
  - Arduino
    - Circuit board
    - Jumper wires
  - Sensors
    - CO2 sensor
    - Pressure sensor (?)
    - Flow meter (?)
- Mechanical Parts
  - Ventilation Tubing
  - Filters (bacterial and viral)
  - Pressure valve
  - PEEP valve
- Testing
  - Balloon (“Lung”)

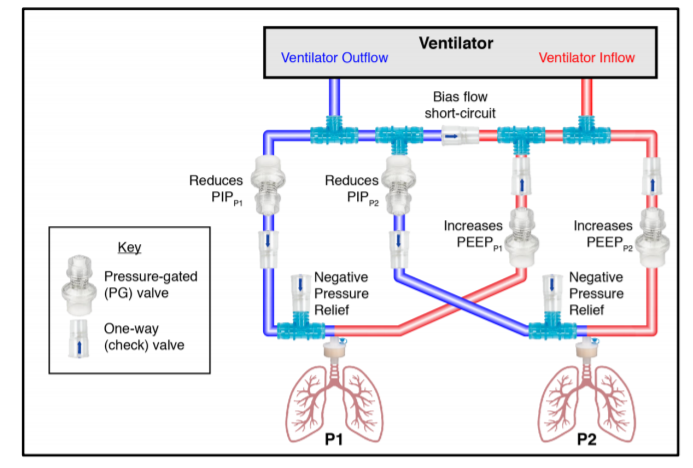
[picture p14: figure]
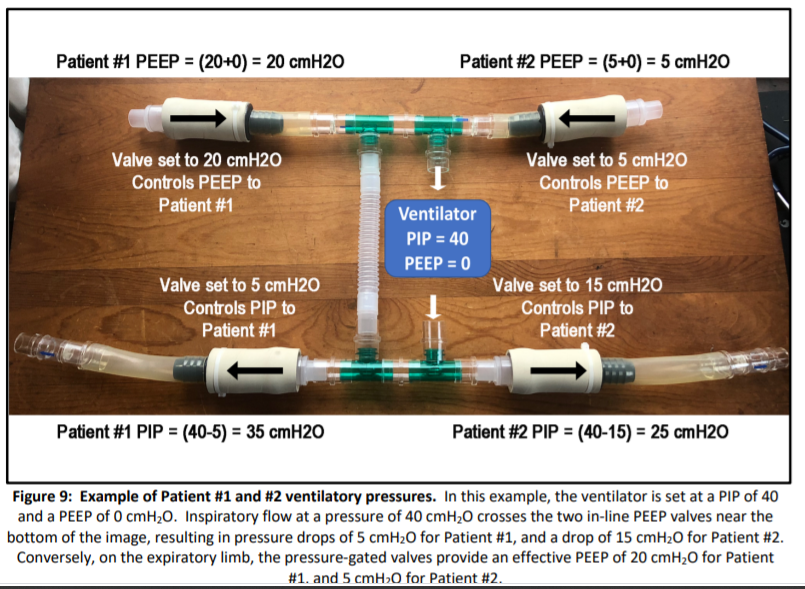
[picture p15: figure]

Notable Characteristics:

- Inspiratory and end-expiratory pressures for each patient can be titrated over time, without changes for one patient affecting the ventilation parameters of the other patient.
- Using in-line spirometry, individual tidal volumes can be measured for each patient.
- Two (or more) patients may be ventilated using a single contemporary ICU ventilator, or using a single contemporary operating room anesthesia machine
- PIP and PEEP are individualized for each patient
- PIP and PEEP can be adjusted for each patient over time, as lung compliance changes
- Valves minimize cross-patient ventilation, even in extreme circumstances such as chest compressions
- Compatible with bacterial and viral filters to minimize infectious cross-contamination
- Compatible with individualized real-time patient spirometry and airway manometry
- Made entirely from off-the-shelf components, no 3D printed or specialty parts needed

Functional Aspects and Limitations:

- Pressure-control ventilation mode is optimal and assumed for this design
- Pressure readouts on the ventilator screen reflect unmodified pressures delivered by the ventilator, and are not representative of what each patient is seeing
- PIP and PEEP for each patient are obtained by adding/subtracting each patient’s valve settings from displayed ventilator settings – see below
- Tidal volume readout on the ventilator is total tidal volume for both patients
- Additional monitors may be deployed in-line for each patient, to measure tidal volumes and airway pressures individually and in real time
- FIO2 and respiratory rate are the same for both patients
- Tidal volumes will differ for each patient, depending on PIP, PEEP and lung compliance
- A short circuit from the ventilator outflow to ventilator inflow is necessary to avoid triggering of circuit occlusion alarm and to allow ventilator bias flow
- Because of changes to the expected circuit, ventilator alarms will not always work as expected, and an alternate alarm strategy must be employed (see discussion below)

Proposed Alarm Settings:

· Shared VTe: Low alarm = Shared VTe – 50 ml, High alarm = Shared VTe + 50 ml, alarm set to trigger if 2 breaths are outside of this range

· Individual VTe (if available): Low alarm = VTe – 50 ml, High alarm = VTe + 50 ml

· Ventilator Ve: Low alarm = Ve – 1 L, High alarm = Ve + 1 L

· Ventilator RR: Low alarm = RR – 3 bpm, High alarm = RR + 3 bpm

· PIP alarm (if available): Low alarm = Set PIP – 5 cmH2O, High alarm = Set PIP + 5 cmH2O

· PEEP alarm (if available): Low alarm = Set PEEP – 2 cmH2O, High alarm = Set PIP + 5 cmH2O

· ETCO2 alarm (if available): Low alarm = Target ETCO2 – 5 mmHg, High alarm = Target ETCO2 + 5 mmHg

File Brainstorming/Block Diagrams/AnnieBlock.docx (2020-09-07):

SETCVMonventilatorappropriately

inspiratory sensor pressureO no O I filter 0 0 O expirator sensor

pressure

r

AMAN spirometer BeBe qq.ua e.qq.fi g

J

C e

ARDUINO

LCDDisplay spirometerpatient tidalvolume readingofeach dowewantto makesome sortofcasing

AnyAlerts isnt ventilatingenough a patient WhereisArduinoDisplayplaced itsnotclunky1 allover patient Doesthis require anypower otherthanfromArduino

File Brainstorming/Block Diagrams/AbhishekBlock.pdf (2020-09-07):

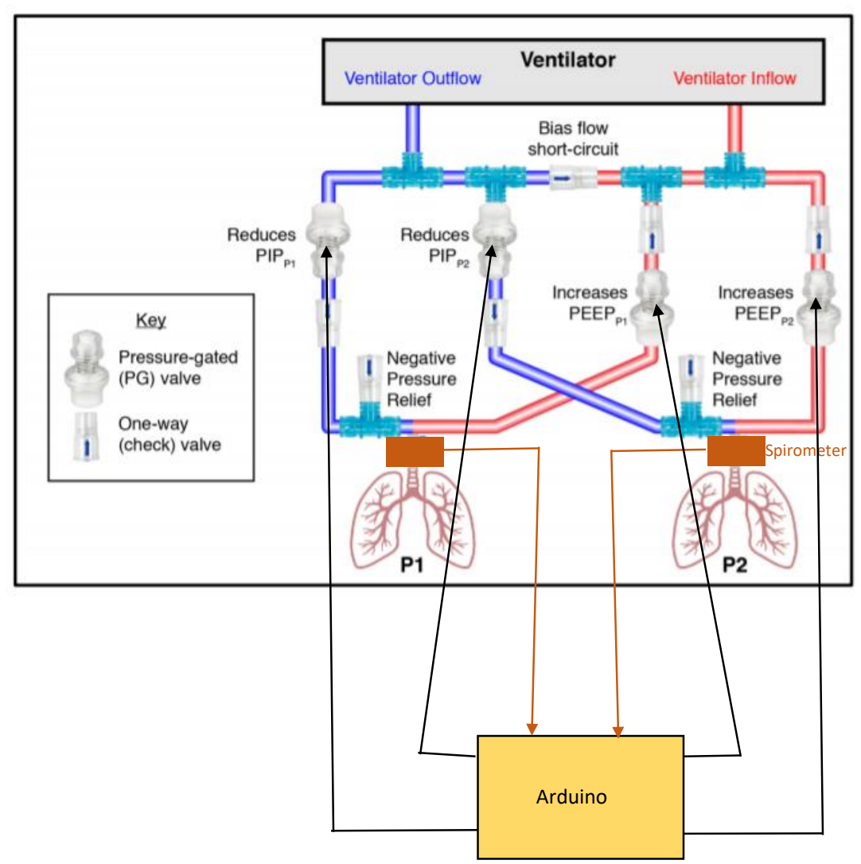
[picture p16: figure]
Arduino; Spirometer

This involves information from the spirometer being fed into the Arduino, and based on the readings from the spirometer, the Arduino will adjust the 4 pressure-gated valves, PG (one inspiratory, one expiratory for each patient) to maintain the optimal spirometer measurements. The diagram on the next page also adds electronic pressure sensors to the first diagram, which can provide feedback about the inspiratory and expiratory pressures supplied to each patient.

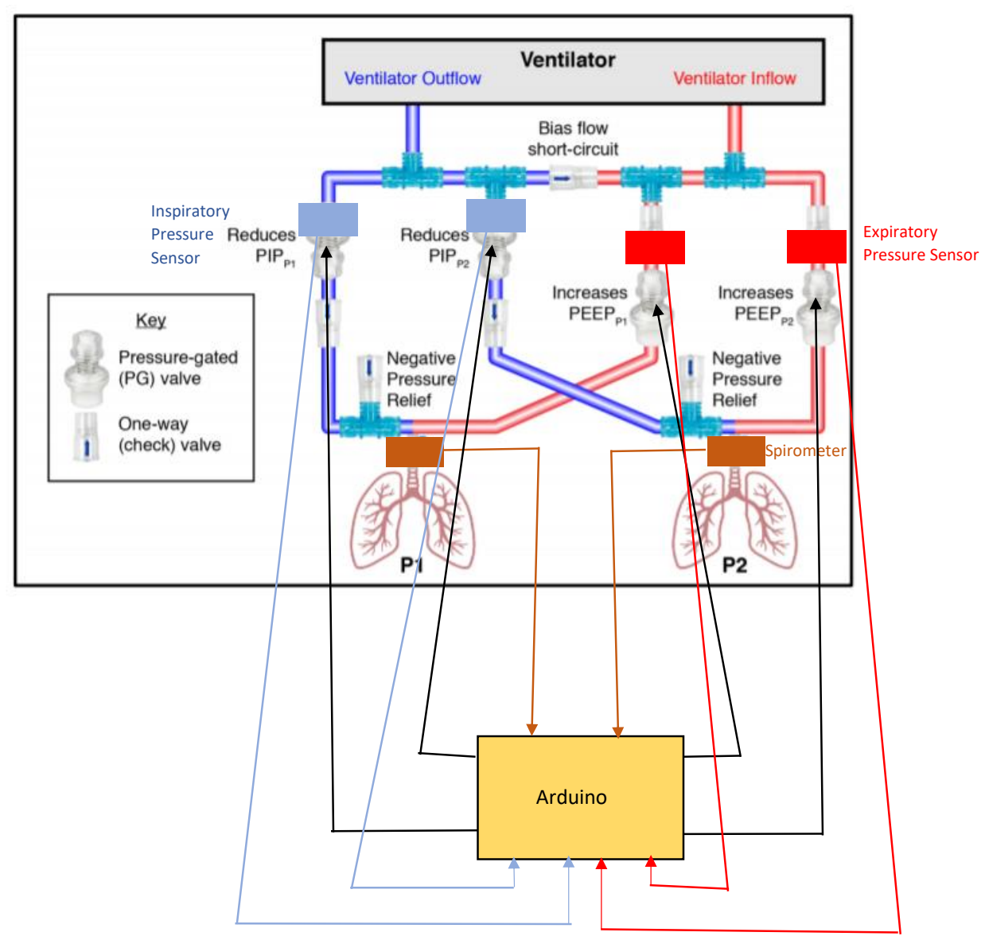
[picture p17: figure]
Arduino; Spirometer; Inspiratory Pressure Sensor; Expiratory Pressure Sensor

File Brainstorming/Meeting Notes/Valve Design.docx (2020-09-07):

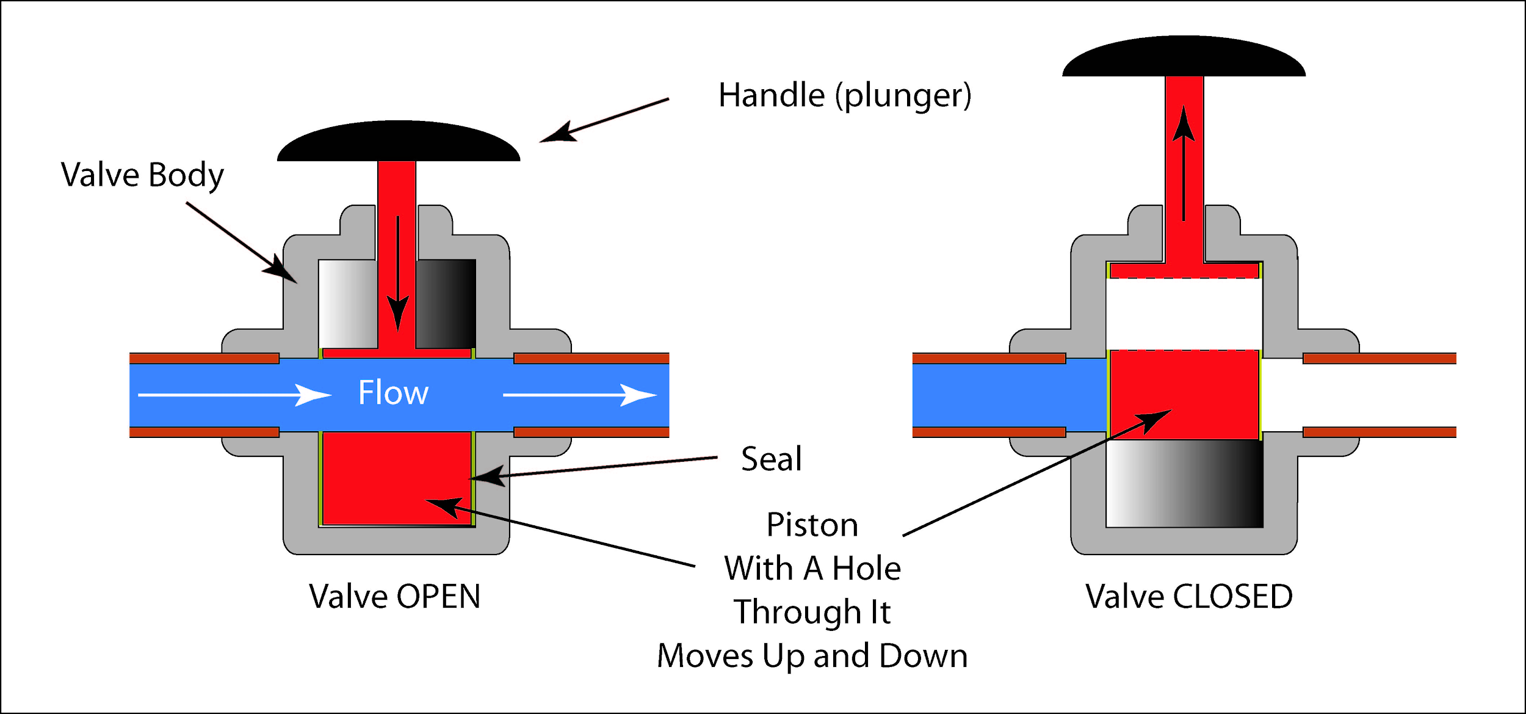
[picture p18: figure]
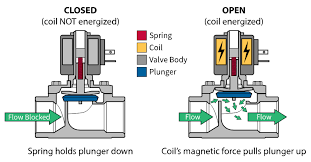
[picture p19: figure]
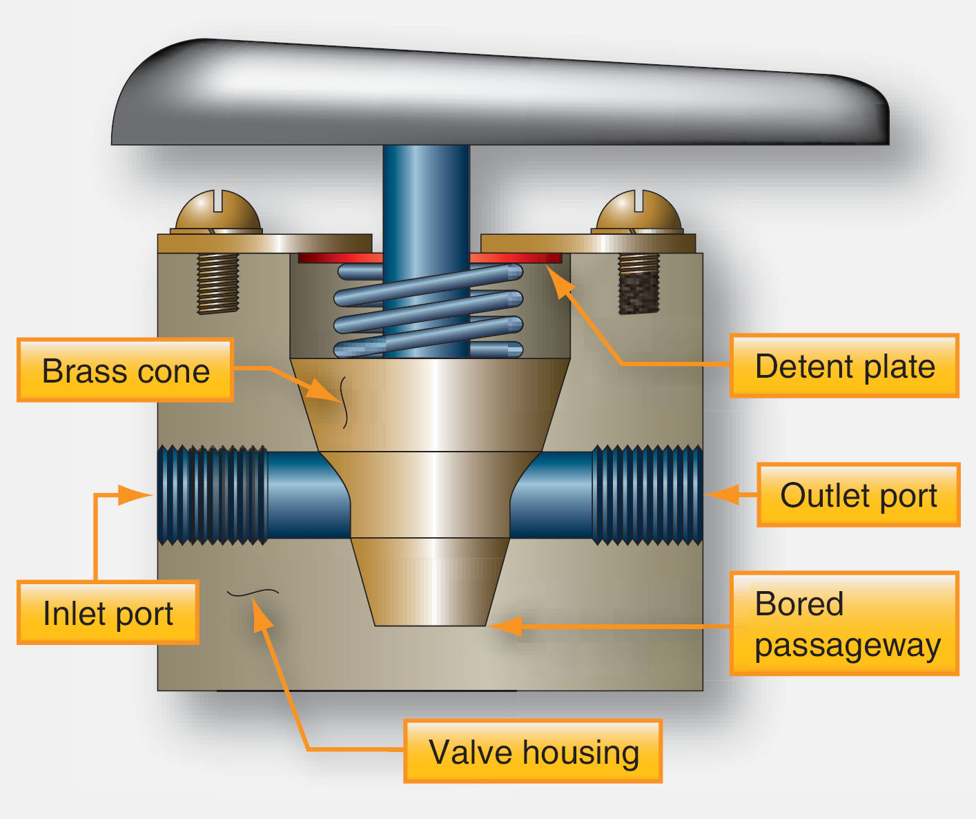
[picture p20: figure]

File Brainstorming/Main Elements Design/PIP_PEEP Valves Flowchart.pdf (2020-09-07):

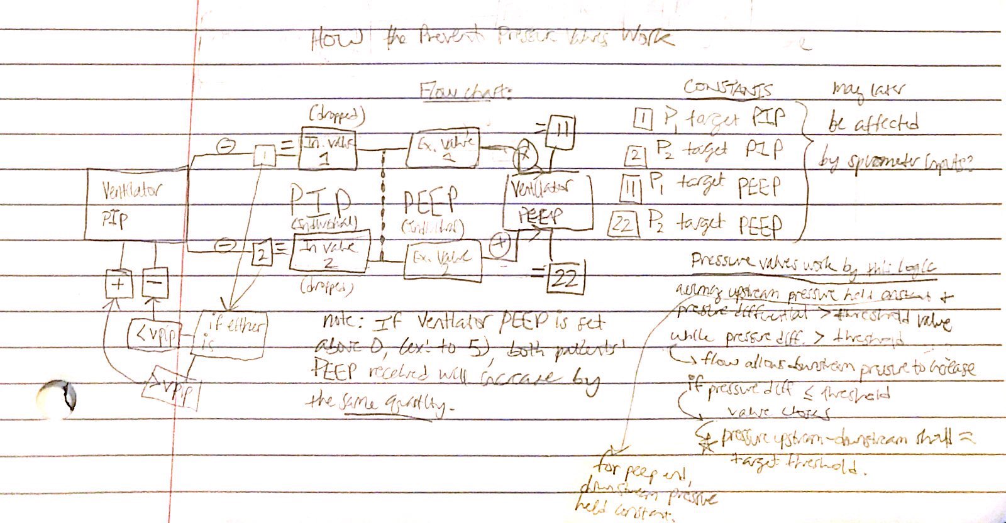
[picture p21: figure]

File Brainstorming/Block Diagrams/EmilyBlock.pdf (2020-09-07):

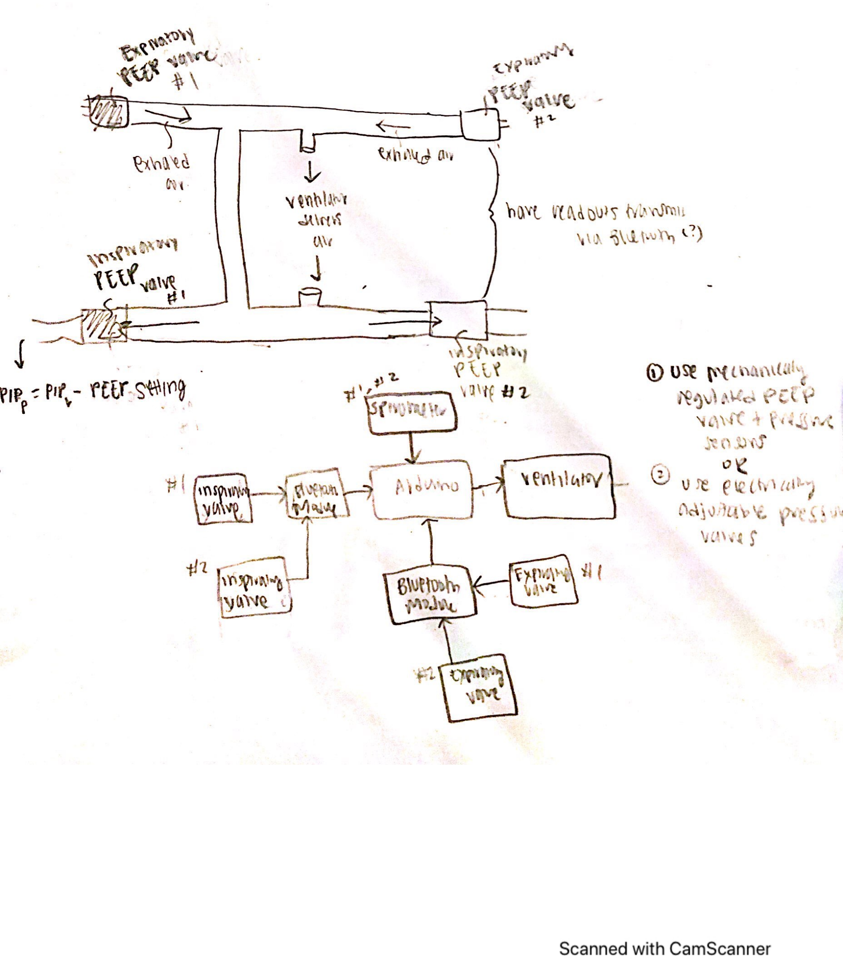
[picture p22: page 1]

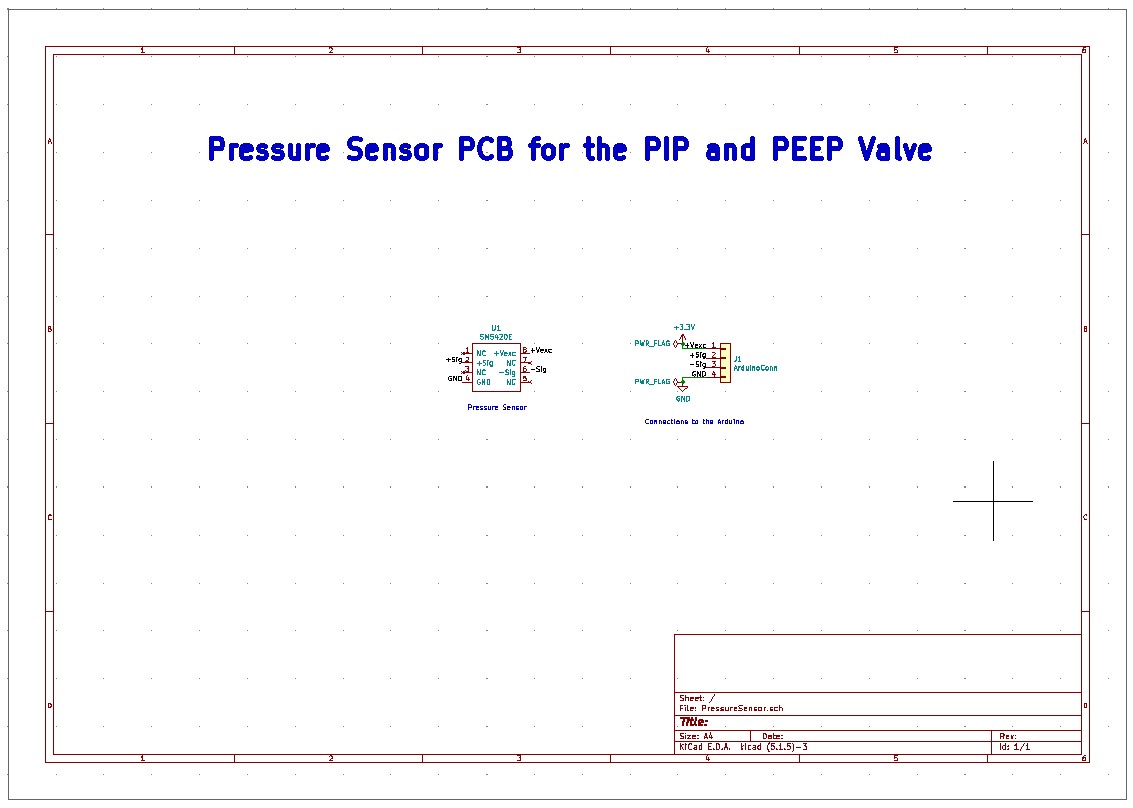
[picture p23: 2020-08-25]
Images/PressureSensor_Schematic.jpg

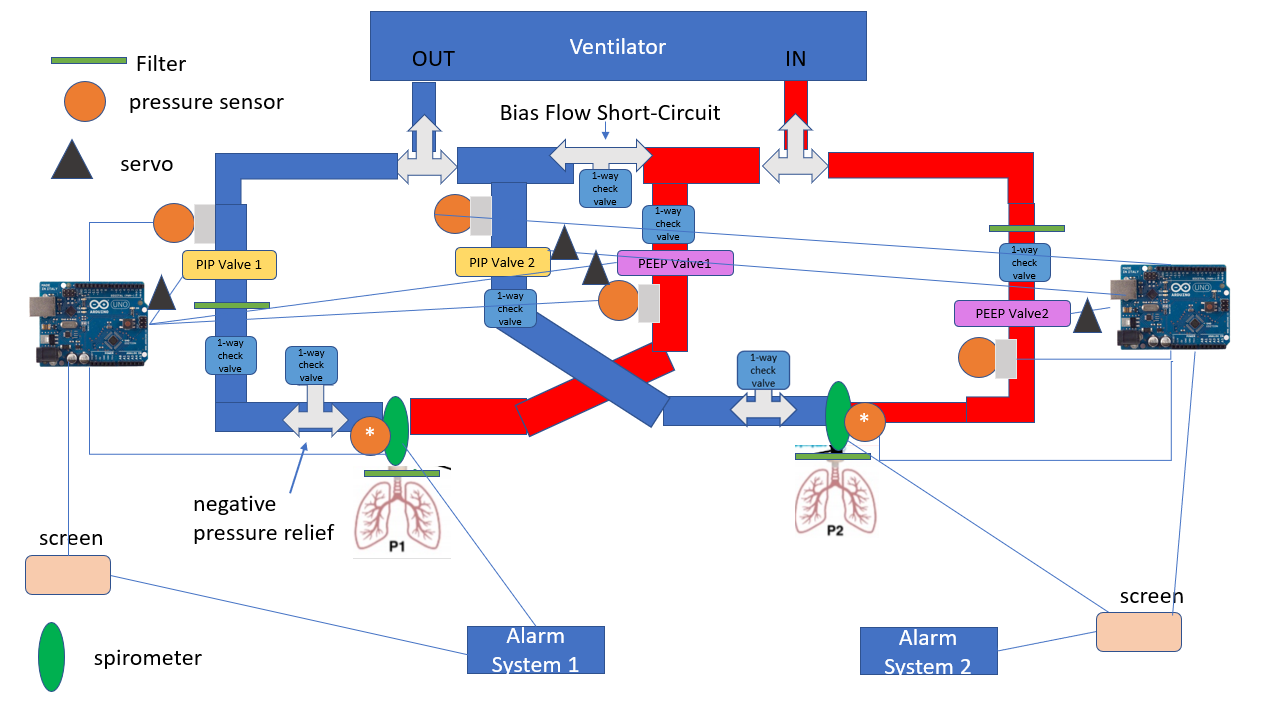
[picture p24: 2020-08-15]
Ventilator_Schematic_Drawing.PNG

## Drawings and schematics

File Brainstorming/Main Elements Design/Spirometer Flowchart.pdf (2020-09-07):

y
b

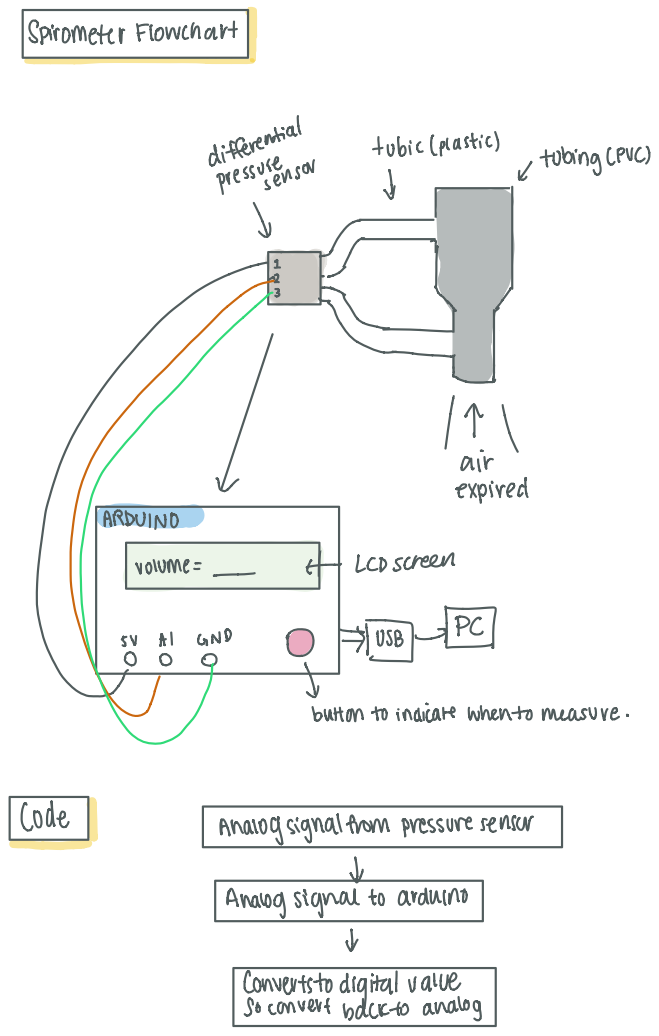
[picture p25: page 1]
SpirometerFlowchart; differential; tubic Plastic; tubing PVC; pressusteensw; PCL; buttontoindicatewhentomeasure; Code; Analogsignalfrompressuresensor; 4 Analogsignalto Arduino tv; convertstodigitalvalue soconvertbackto analog

to

## dP z fate IT

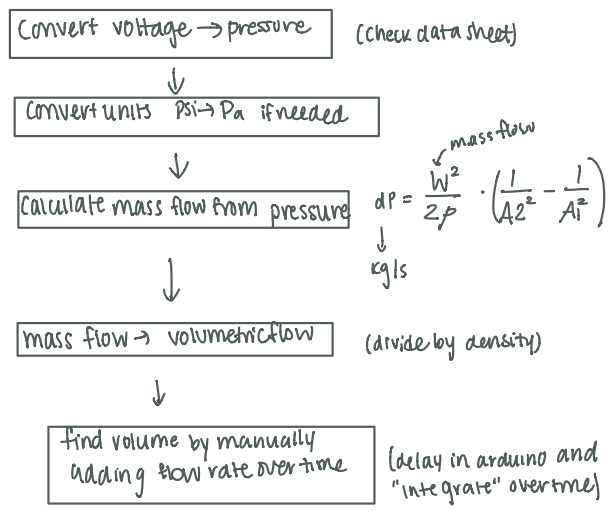
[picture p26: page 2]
convertvoltage pressure; checkdatasheet; convertunits Psi7Pa ifneeded; massflow; calculatemass; flow frompressure; Kgb; massflow 7 Volumetricflow; dividebydensity; I findvolumebymanually; adding It wrateovertime; delay inarduinoand; integrate overtime

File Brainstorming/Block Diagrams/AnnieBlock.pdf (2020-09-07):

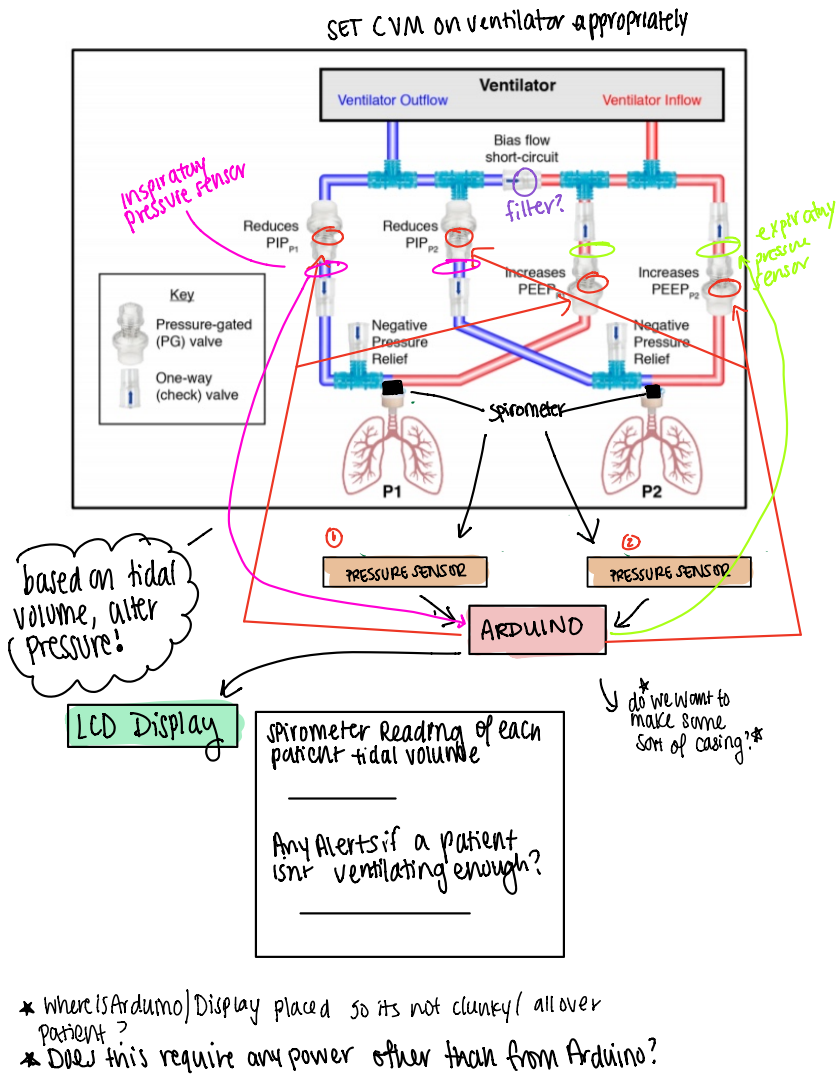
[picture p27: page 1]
SETCVMonventilatorappropriately; inspiratory; pressure; sensor; filter; expirator O; AMAN; BeBe; spirometer; ARDUINO; dowewantto; LCDDisplay spirometerreadingofeach; makesome; patient tidalvolume; sortofcasing; WhereisArduinoDisplay placed; itsnotclunky1 allover

AnyAlerts a patient isnt ventilatingenough

patient
Doesthis require anypower otherthanfromArduino

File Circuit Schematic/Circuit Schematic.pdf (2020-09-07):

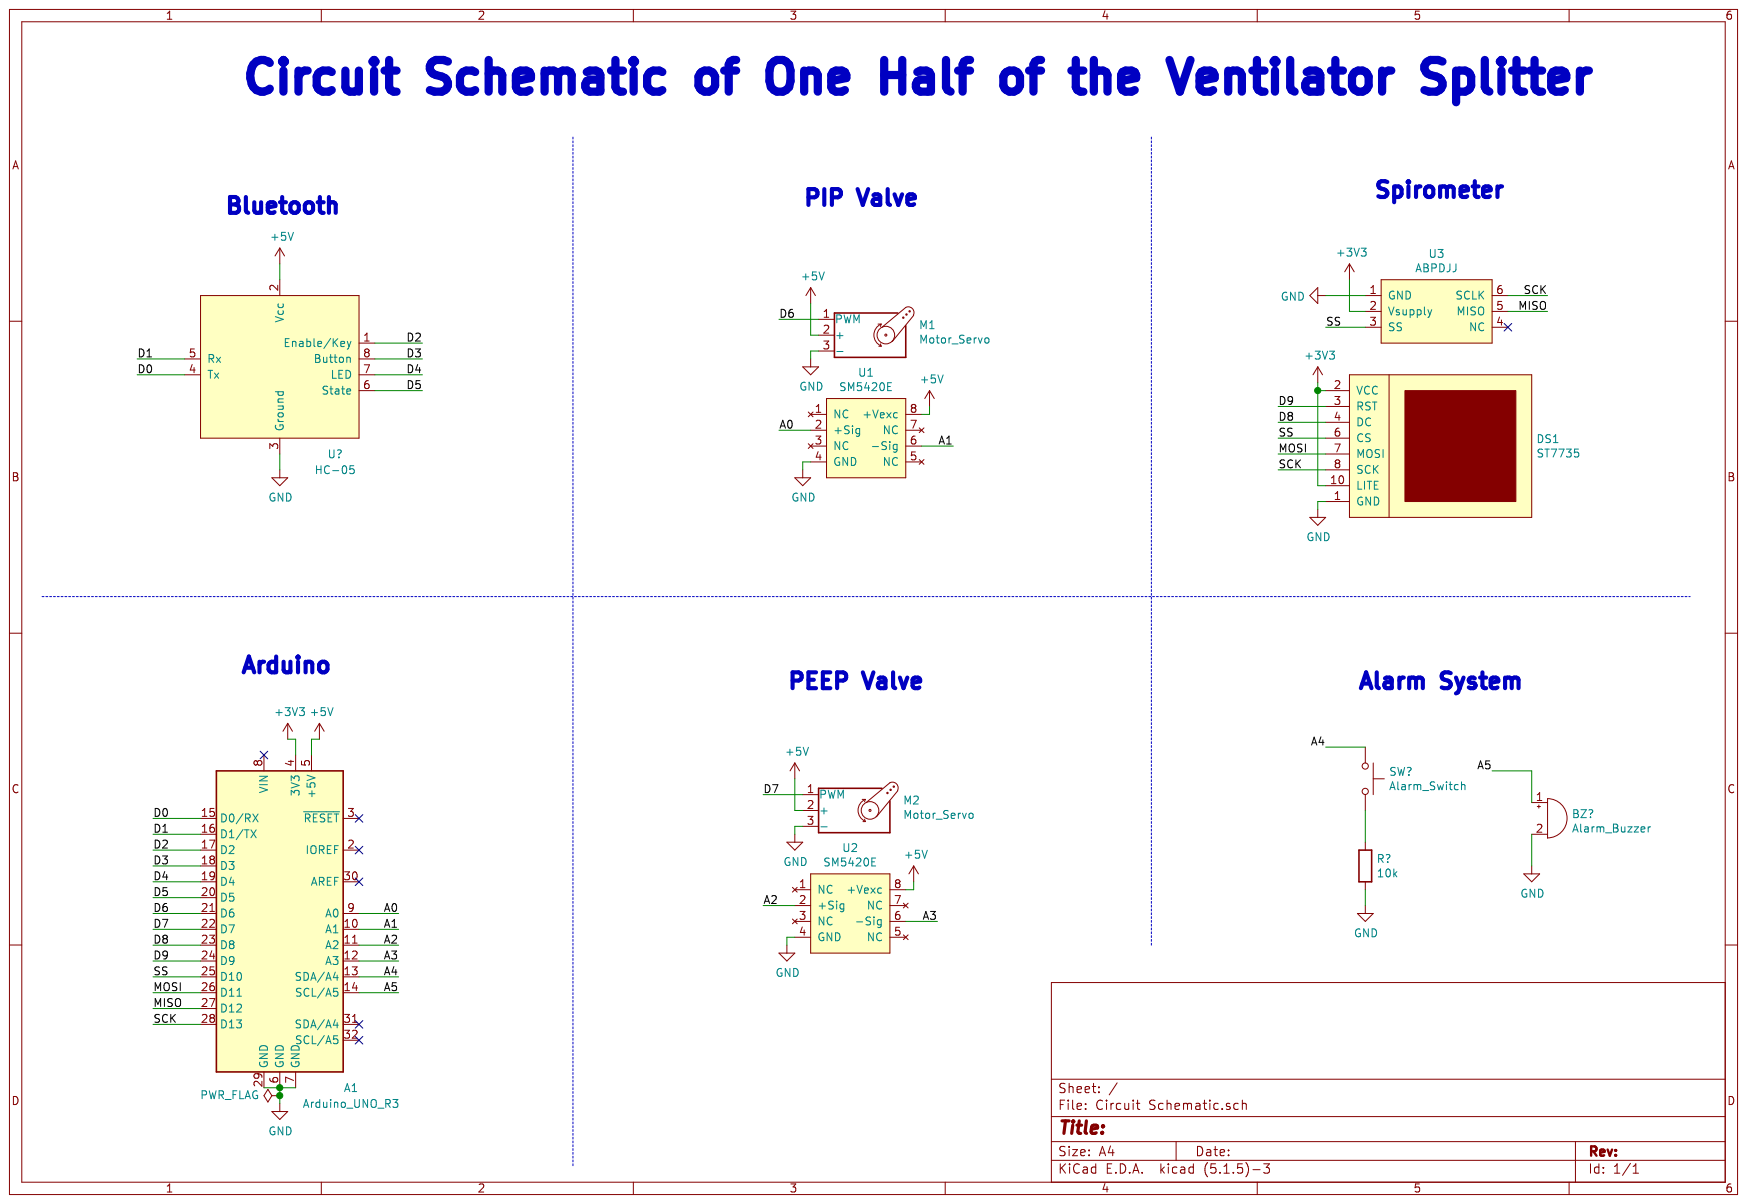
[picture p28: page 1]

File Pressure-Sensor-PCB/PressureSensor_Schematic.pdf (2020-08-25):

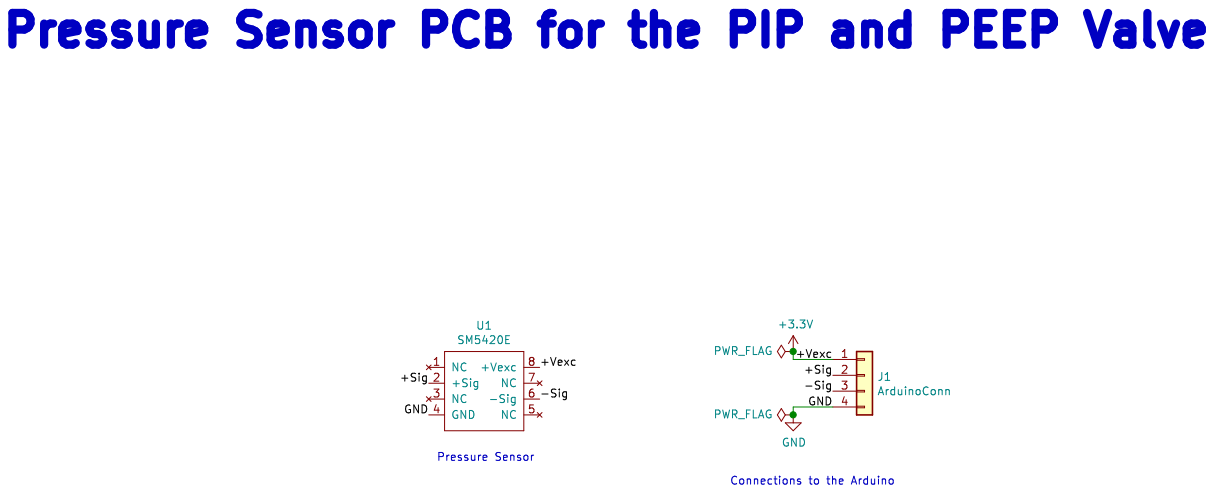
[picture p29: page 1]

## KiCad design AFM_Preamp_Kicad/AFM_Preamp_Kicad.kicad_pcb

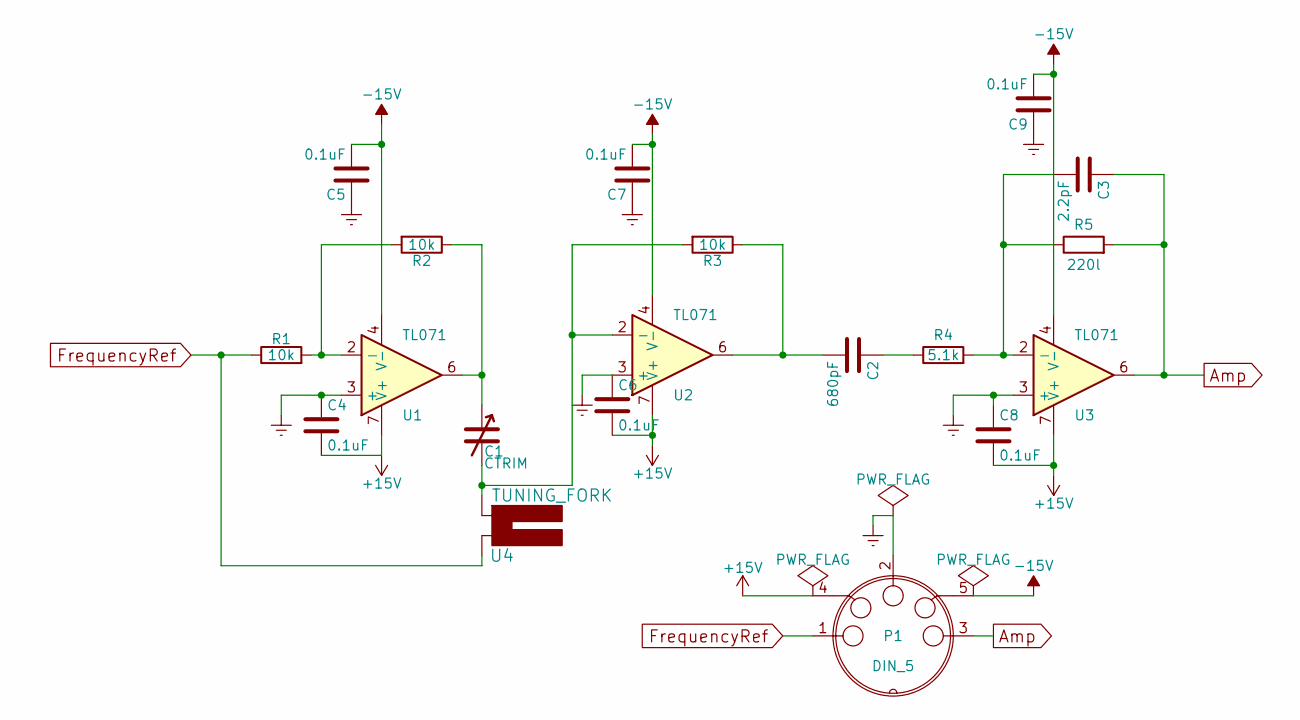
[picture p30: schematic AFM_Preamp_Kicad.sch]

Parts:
C1: CTRIM; C_Radial_D10_L13_P5
C2: 680pF; C_Disc_D3_P2.5
C3: 2.2pF; C_Disc_D3_P2.5
C4, C5, C6, C7, C8, C9: 0.1uF; C_Disc_D3_P2.5
P1: DIN_5; Pin_Header_Straight_1x05
R1, R2, R3: 10k; Resistor_Horizontal_RM10mm
R4: 5.1k; Resistor_Horizontal_RM10mm
R5: 220l; Resistor_Horizontal_RM10mm
U1, U2, U3: TL071; DIP-8_W7.62mm
U4: TUNING_FORK; Pin_Header_Straight_1x02

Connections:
+15V: C4.2, C6.2, C8.2, P1.4, U1.7 (V+), U2.7 (V+), U3.7 (V+)
-15V: C5.2, C7.2, C9.2, P1.5, U1.4 (V-), U2.4 (V-), U3.4 (V-)
Amp: C3.1, P1.3, R5.2, U3.6
Earth: C4.1, C5.1, C6.1, C7.1, C8.1, C9.1, P1.2, U1.3 (+), U2.3 (+), U3.3 (+)
FrequencyRef: P1.1, R1.1, U4.1
unnamed: C1.1, R2.1, U1.6
unnamed: C1.2, R3.2, U2.2 (-), U4.2
unnamed: C2.1, R4.1
unnamed: C2.2, R3.1, U2.6
unnamed: C3.2, R4.2, R5.1, U3.2 (-)
unnamed: R1.2, R2.2, U1.2 (-)

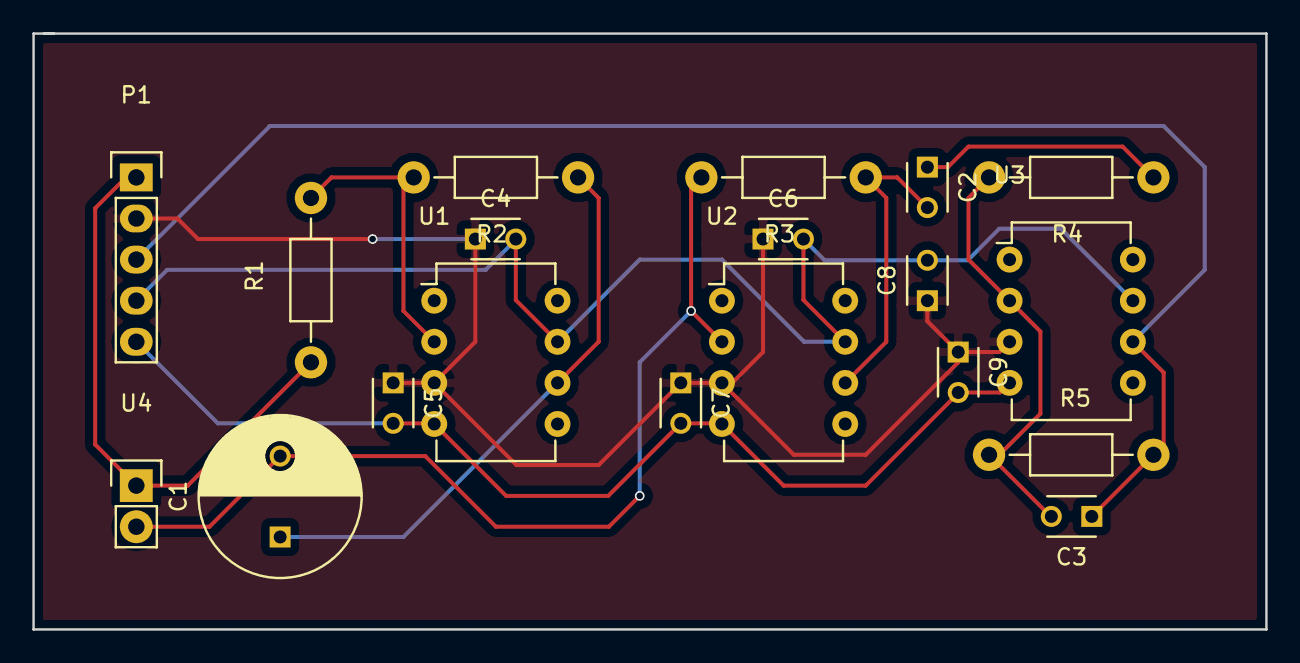
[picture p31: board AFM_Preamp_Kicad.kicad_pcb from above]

Board: 2 copper layers, 76.2 x 36.8 mm, 19 parts (0 on the bottom side), 11 nets.

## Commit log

2020-07-29 Adds Pressure Sensor PCB
    [PressureSensor-B_Cu.gbr, PressureSensor-B_Mask.gbr, PressureSensor-B_Paste.gbr, PressureSensor-B_SilkS.gbr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]
2020-08-15 Adds circuit schematics
    [Circuit Schematic.kicad_pcb, Circuit Schematic.sch]
2020-08-25 Adds schematic PDFs and images
    [PressureSensor.sch]
2020-09-07 Updates schematic to include bluetooth module and alarm system components
    [Circuit Schematic.sch]
2020-09-07 Updated buzzer connections
    [Circuit Schematic.sch]
2020-09-07 Fixes bulleted materials in README
